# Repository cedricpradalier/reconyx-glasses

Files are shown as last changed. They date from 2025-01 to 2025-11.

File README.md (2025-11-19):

# reconyx-glasses
3D model of lens holders for the [Reconyx HyperFire](https://www.reconyx.com/product/Outdoor_Series?gad_source=1) cameras.

Original camera from the manufacturer's website

This repository includes some work on 3D models dedicated to attach a lens to the camera. The HyperFire camera is a rugged system designed for wild-life monitoring. As a result, the lens focus is fixed to infinity (a few meters away from the camera) and cannot be changed. In our application where the camera takes pictures of images relatively close to the lens, this leads to blurry images. Although this is not a problem in its normal use case, the camera is far-sighted (or even presbyopic) for our very specific use case (probably outside of the camera specifications in the first place) and it needs prescription glasses. 

## Objectives
In our use case, observing toads, tritons and salamanders in wildlife underpass, the effect is the following:

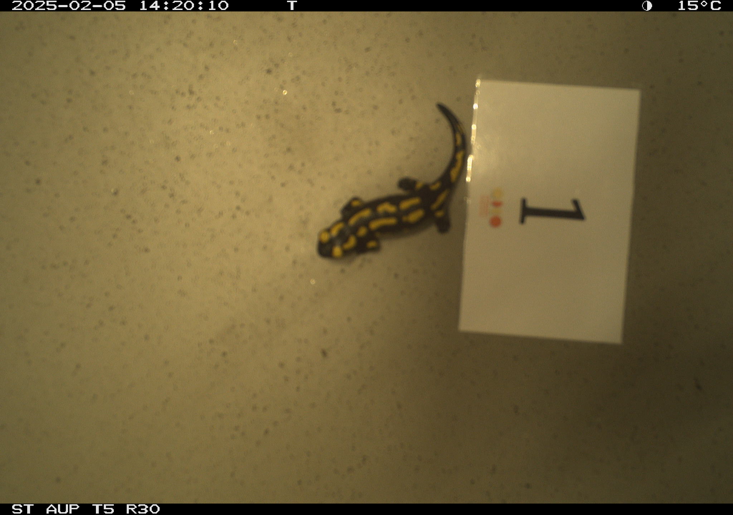
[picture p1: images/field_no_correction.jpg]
Original camera no correction


With the proper correction:

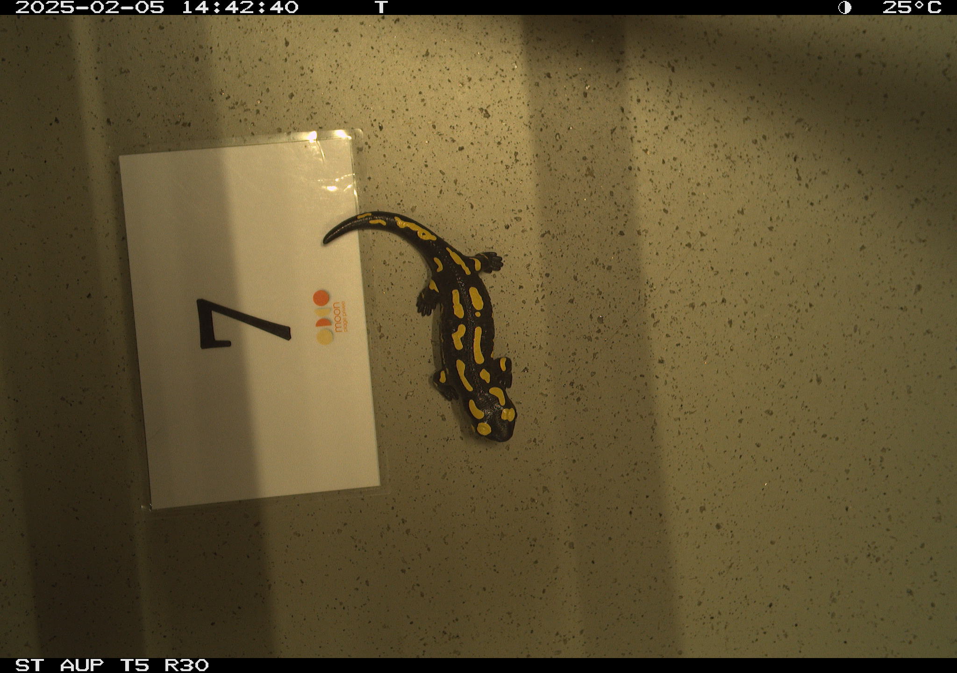
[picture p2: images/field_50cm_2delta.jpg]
Original camera correction


## Designs
The resulting lens holder is designed with [OpenSCAD](https://openscad.org/) to be 3D printed. The SCAD files are in the [scad](scad) folder. The resulting STL files in the [stl](stl) folder.

### Magnetic design
The [third design](stl/reconyx_magnets.stl) is made to be installed on the enclosure and kept in place with magnets. It is not secured as strongly as the previous designs, but much easier to install in cramped condition. This designed is parameterized by the magnet size (10mm diameter, 3mm thickness in the picture below). A 3D view of one version of the design is visible here: 

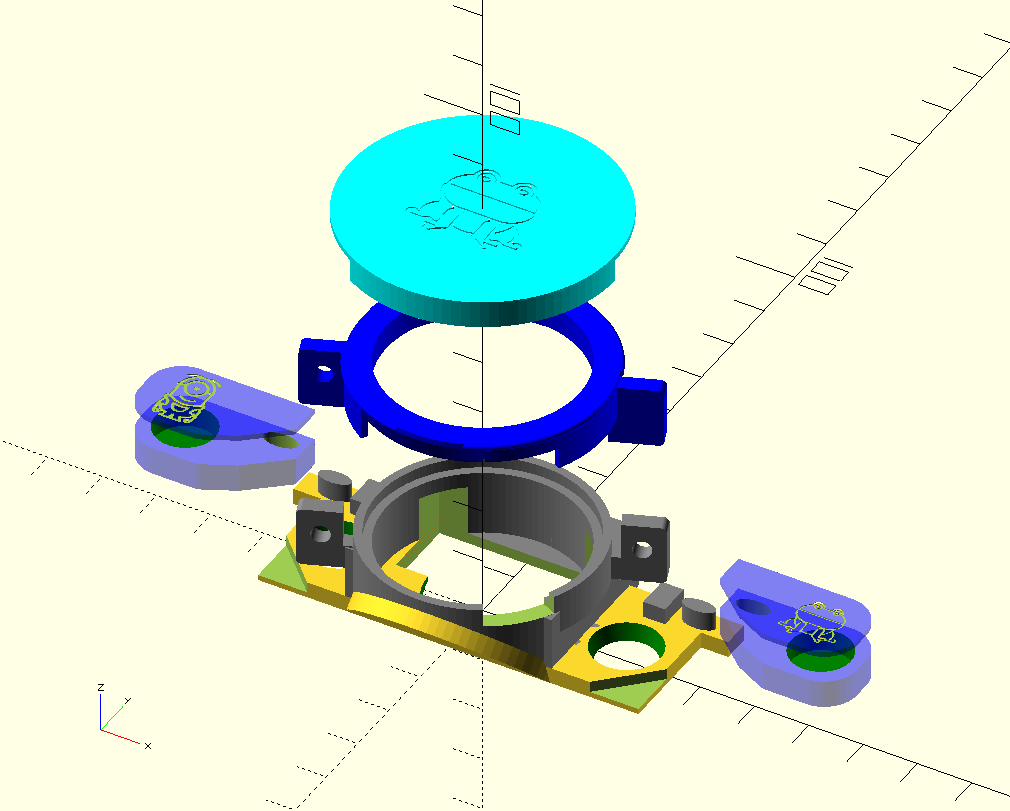
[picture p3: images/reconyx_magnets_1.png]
camera with magnet 1


After printing, the magnets need to be inserted in the side flap (purple in the image above) and the flap cover glued (we use a standard office glue with our PLA print). The flap can then be glued to the main body. 

Once the lens is inserted into the design, the top part(dark blue here) is placed on top of it and rotated into place. A small screw (3mm diameter, 10mm length) is then used to secure the assembly. The top cover (light blue here) is used to protect the lens while the assembly is in storage.

A finalized version, can be seen here with the additional engraving, and installed on the camera

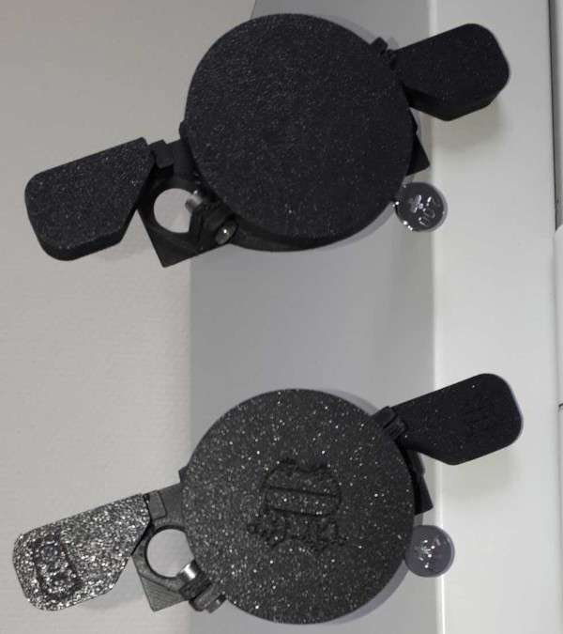
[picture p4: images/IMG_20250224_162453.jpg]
camera with magnet 2


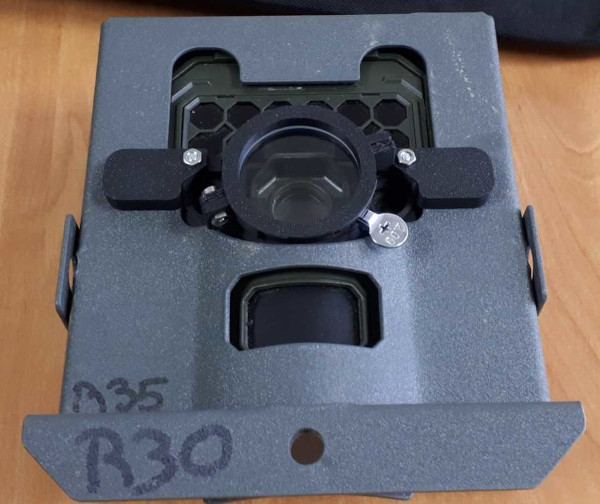
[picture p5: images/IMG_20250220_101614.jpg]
camera with magnet 3


Note that the design was thought to be printed on a filament printer. If you print in a medium that does not rely on support matterial, you can use this [alternative model](stl/reconyx_magnets_no_support.stl). In this design the magnet flap are rigidly attached to the model.

### Mechanically locked design
The [second design](stl/reconyx_box.stl) is kept in place by the [Reconyx enclosure box](https://www.reconyx.com/product/HyperFire-2-Security-Enclosure).

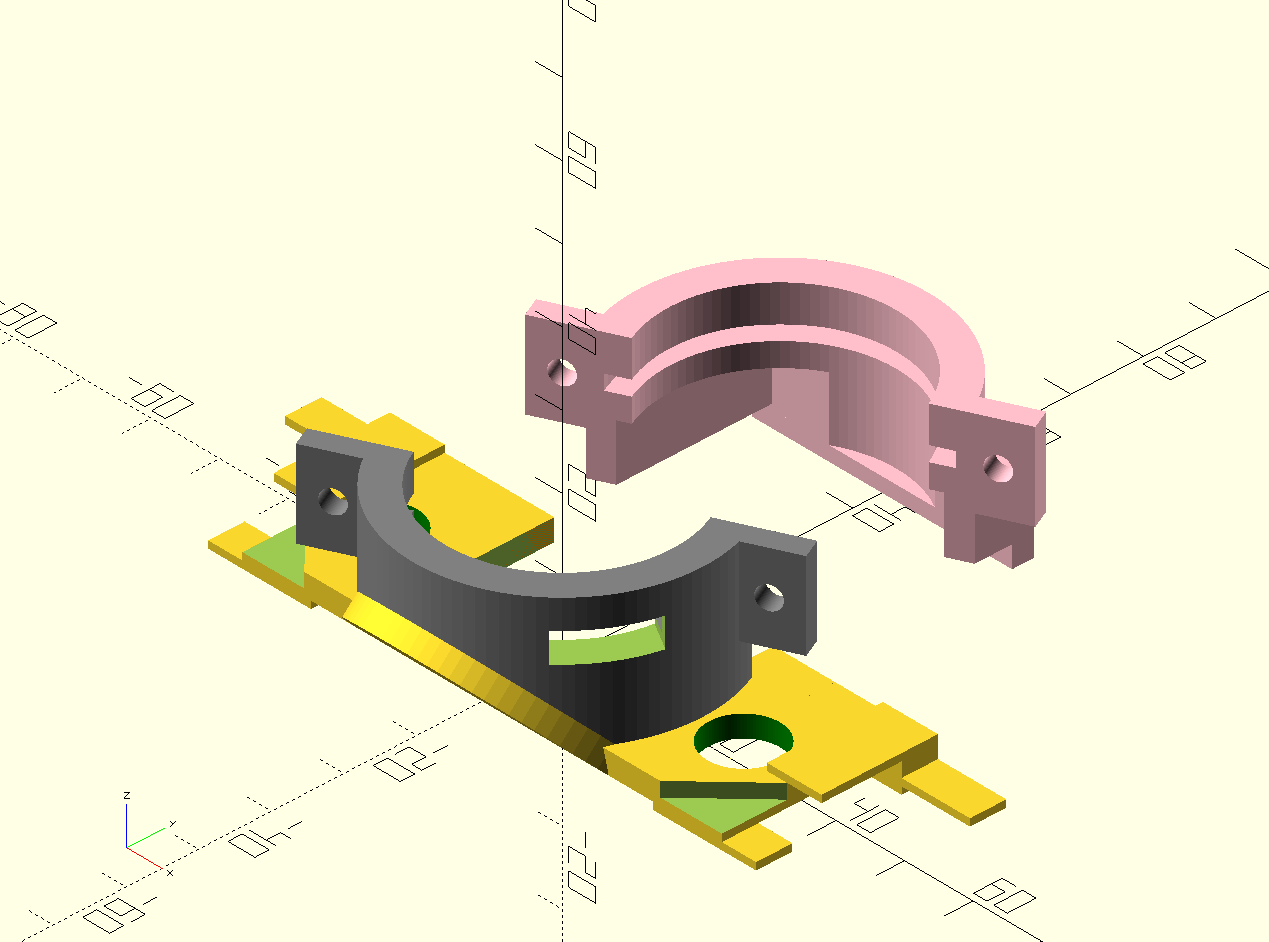
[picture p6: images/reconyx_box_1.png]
camera with clipped lenses CAD


The camera, in its enclosure, with the lens on is displayed here:

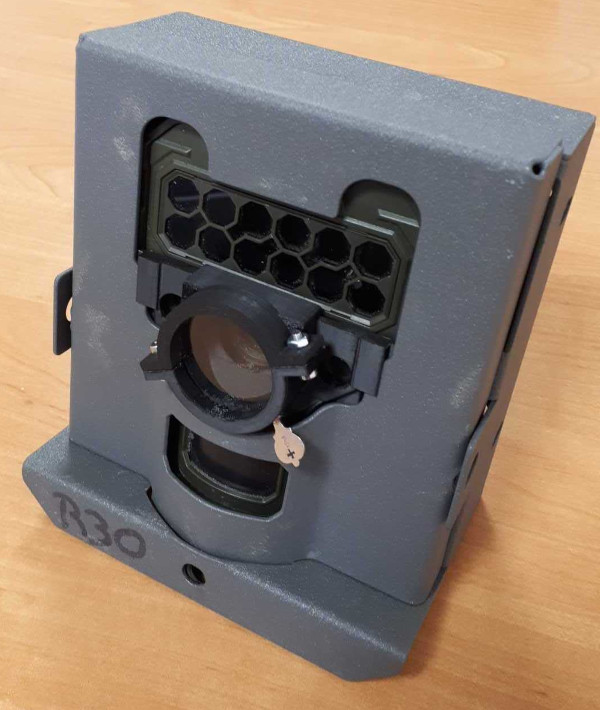
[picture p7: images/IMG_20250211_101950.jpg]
camera with box lens


Adding a tiny rubber band forces the lens in place, while keeping a little bit of flexibility when opening or closing the enclosure:

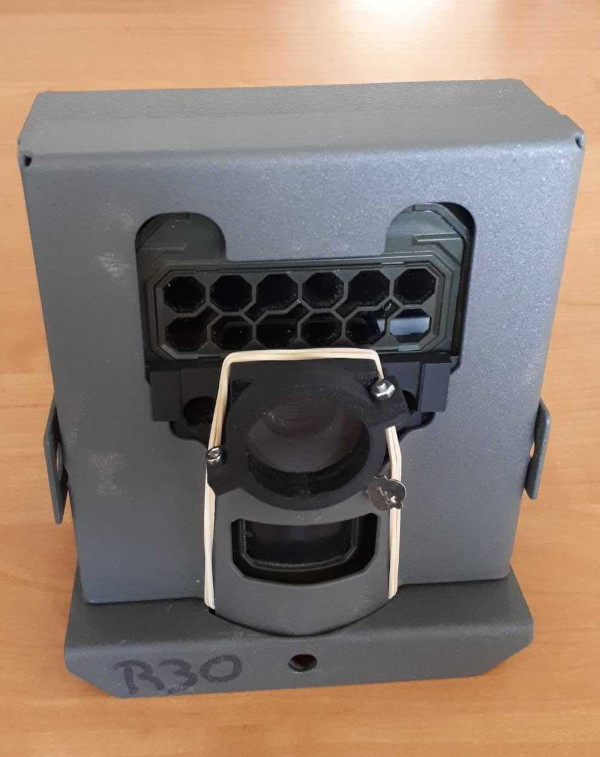
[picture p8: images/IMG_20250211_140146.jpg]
camera with box lens and rubber


### Direct clip design
The [first design](stl/reconyx_clip.stl) clips on the camera without any enclosure. 
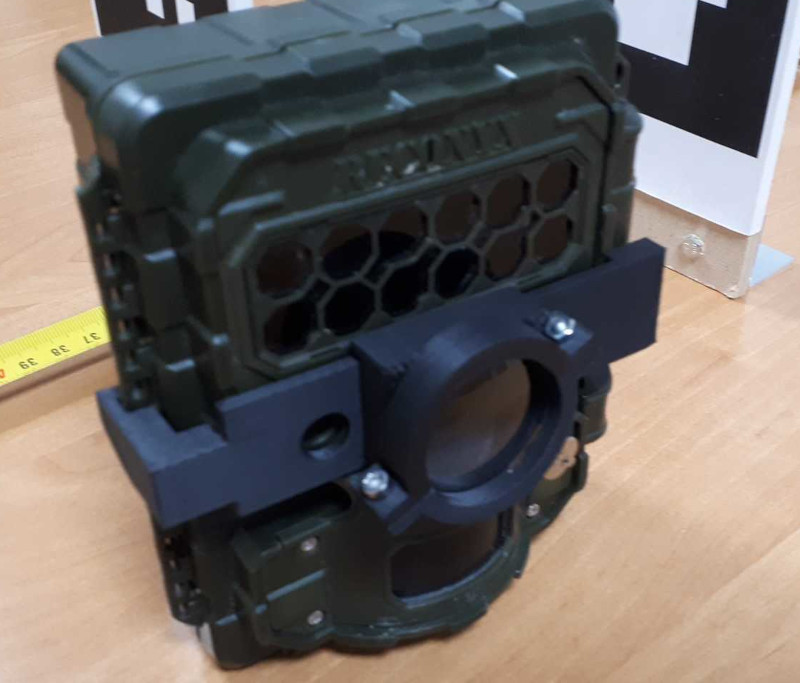
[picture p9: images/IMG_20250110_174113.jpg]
camera with clipped lenses


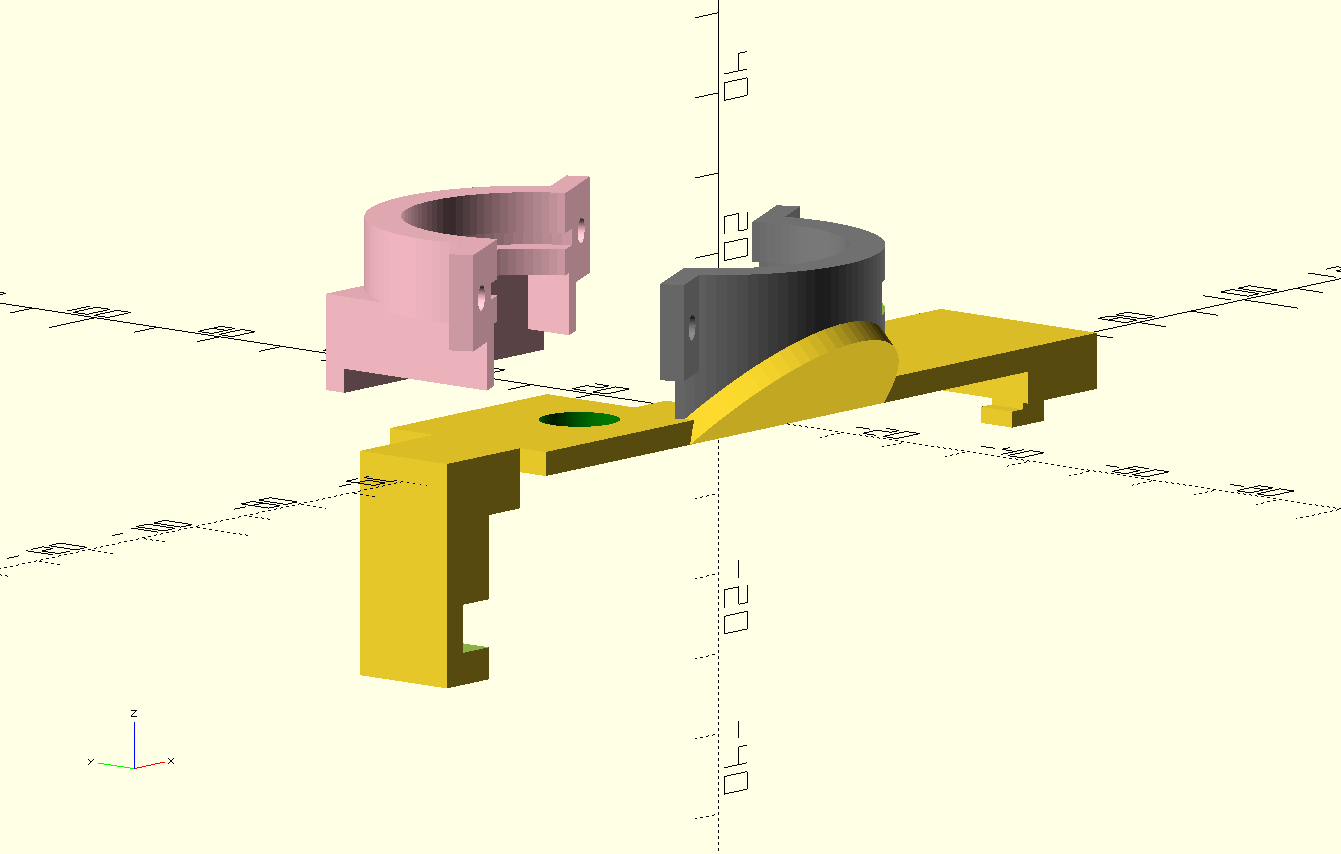
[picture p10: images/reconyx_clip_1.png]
camera with clipped lenses CAD1


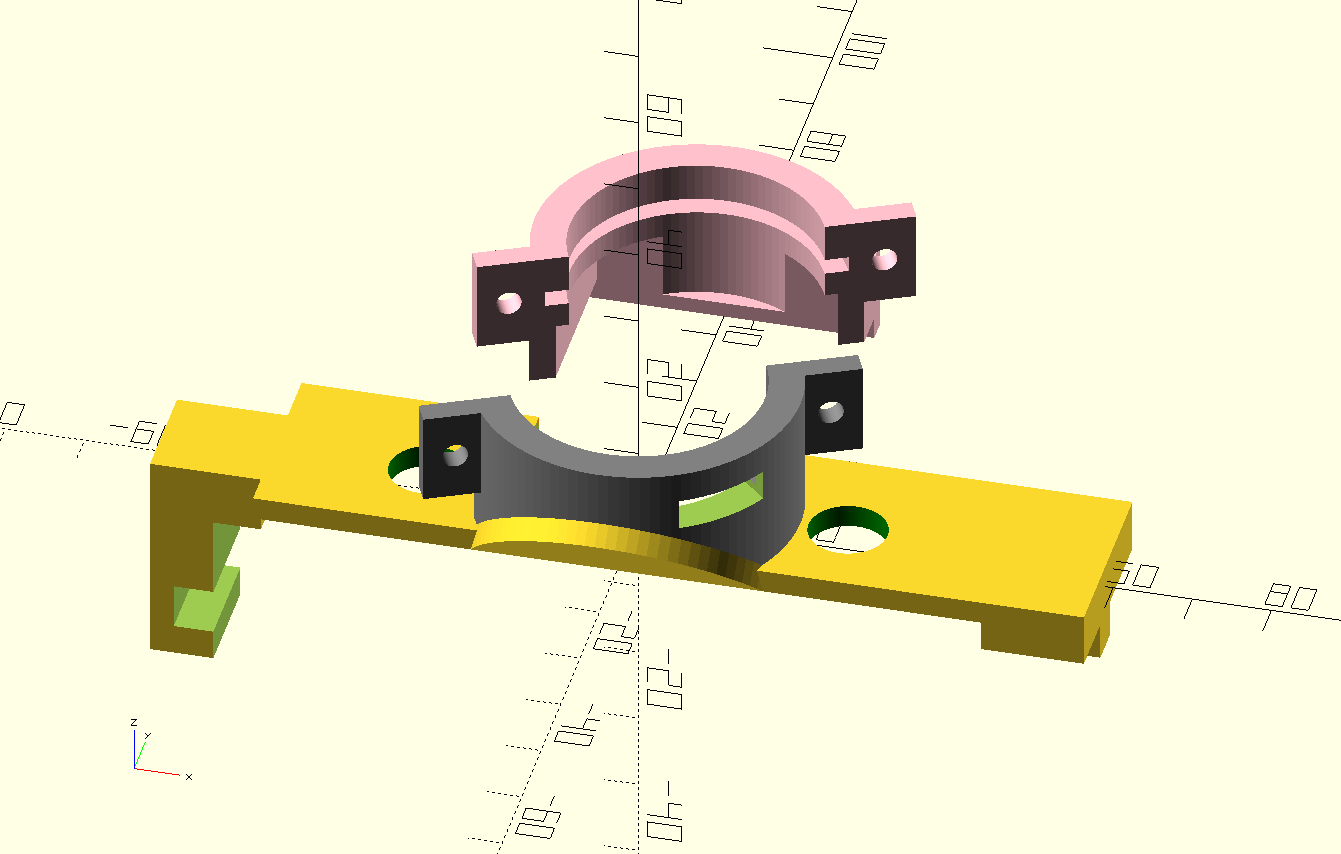
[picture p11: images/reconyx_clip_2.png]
camera with clipped lenses CAD2


## Finding lenses

The proposed model is designed to hold [optometrist test lenses](https://fr.aliexpress.com/item/1703330056.html), which are 38mm wide and 2mm thick. It is relatively easy to find 40mm lenses as [high-school optics material](https://jeulin.com/ovio_fr/pr-323333.html). This can be changed with the Dlens and Tlens variables in the scad files. 

The rule of thumb for selecting the focal or the dioptries is simple. The focal should approximately be equivalent to the distance at which the animals are going to be imaged. The focal resulting from a lens is the inverse of the dioptries, in m. 

Dioptries | Distances
--- | ---
1 | 1.00 m
2 | 0.50 m
2.5 | 0.40 m
3 | 0.33 m
4 | 0.25 m

## Lens testing
After some testing with my [optometrist](https://www.remillyoptic.fr/), this is the effect of choosing glasses from +2.0 to 3.0 dioptries, to observe an object 40cm away from the camera.
Without lenses:
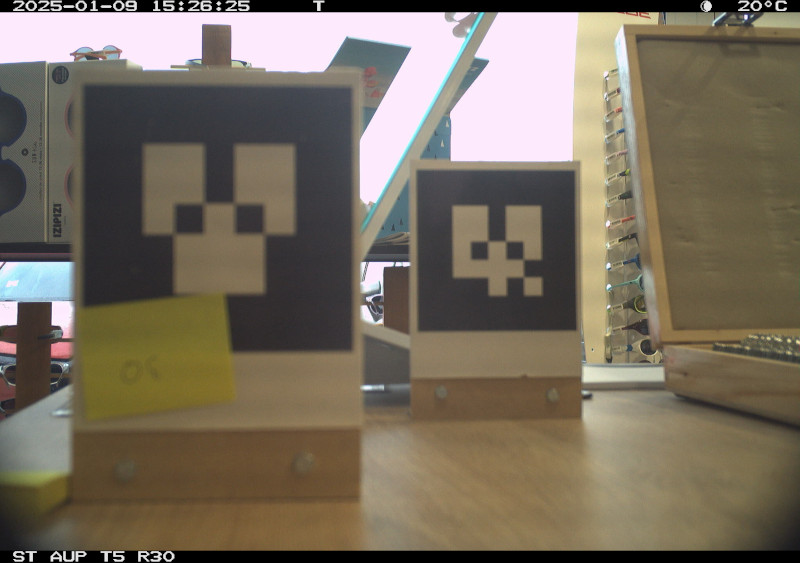
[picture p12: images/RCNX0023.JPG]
Naked lens


With +2.0 correction:
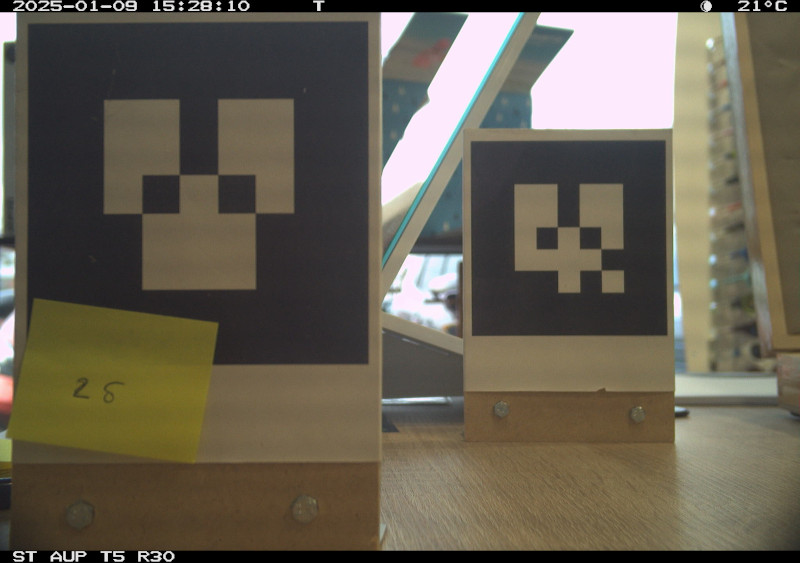
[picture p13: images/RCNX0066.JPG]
+2.0 dioptries


With +2.5 correction:
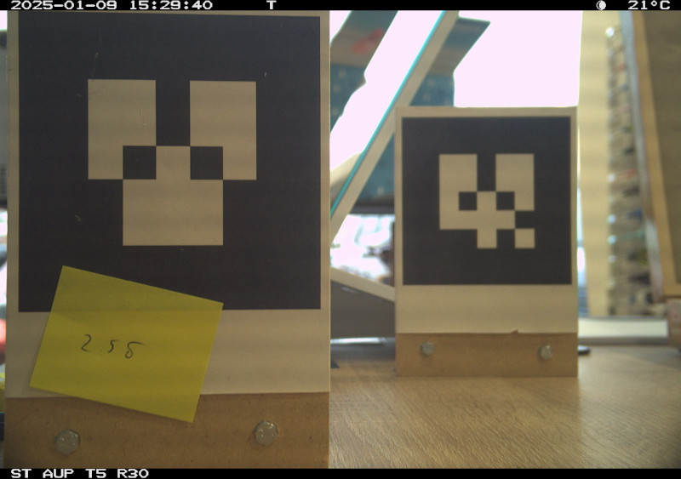
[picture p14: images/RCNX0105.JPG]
+2.5 dioptries


With +3.0 correction:
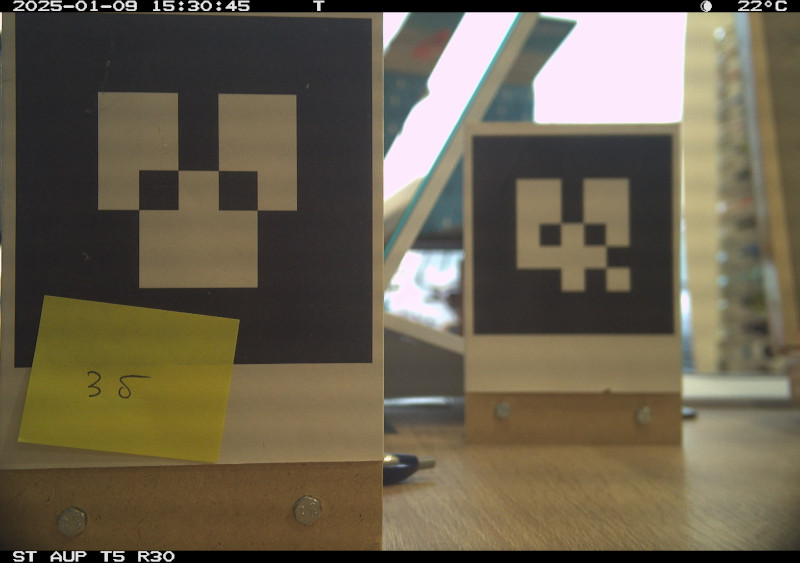
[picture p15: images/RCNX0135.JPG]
+3.0 dioptries


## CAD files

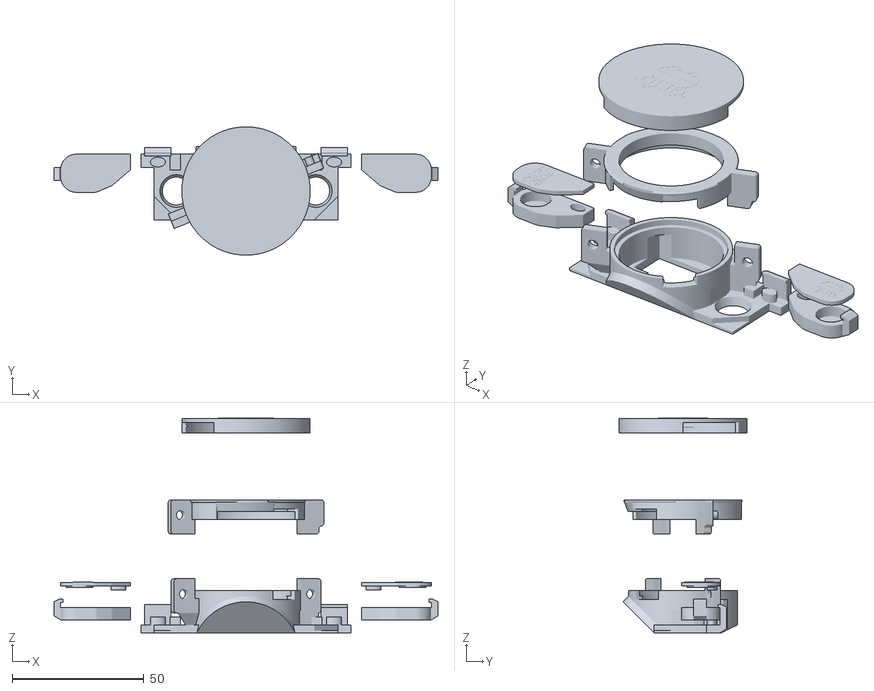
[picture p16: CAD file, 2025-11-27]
stl/reconyx_magnets.stl
146.0 x 48.8 x 81.7

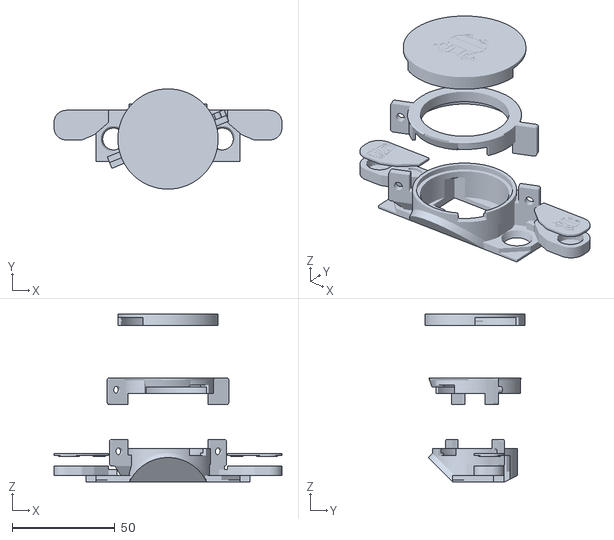
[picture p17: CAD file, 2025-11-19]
stl/reconyx_magnets_no_support.stl
111.0 x 48.8 x 81.6

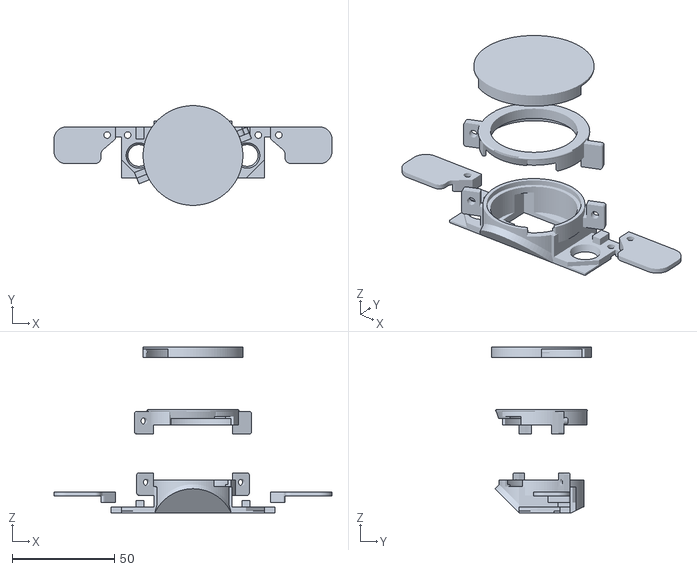
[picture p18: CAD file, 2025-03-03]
stl/reconyx_magnets_large.stl
136.0 x 48.8 x 81.1

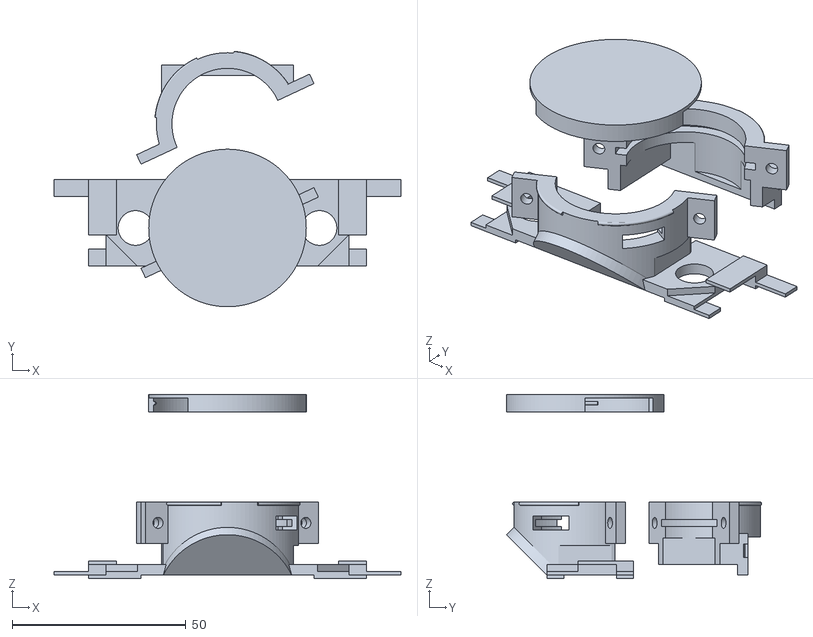
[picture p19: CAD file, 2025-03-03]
stl/reconyx_box.stl
100.0 x 73.6 x 53.0

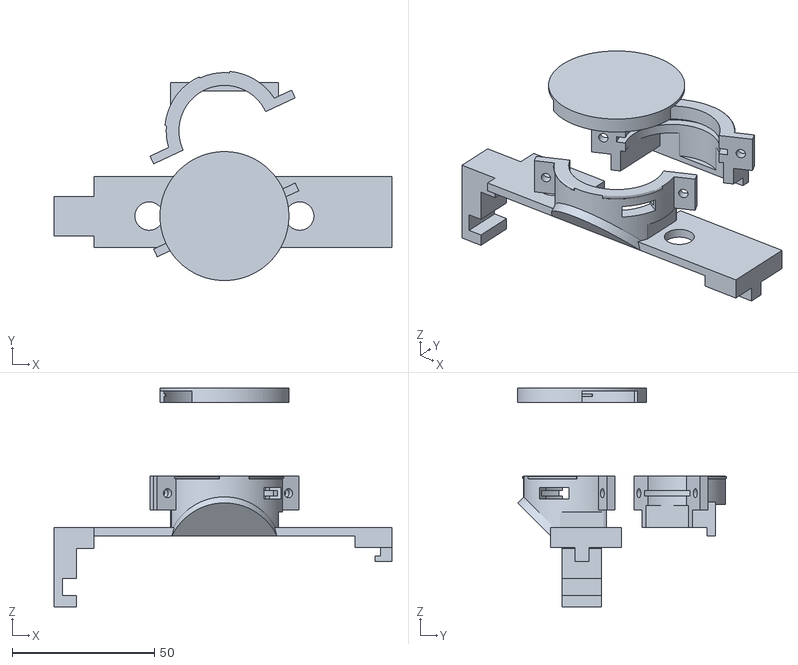
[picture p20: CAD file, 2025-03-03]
stl/reconyx_clip.stl
119.0 x 73.6 x 77.0

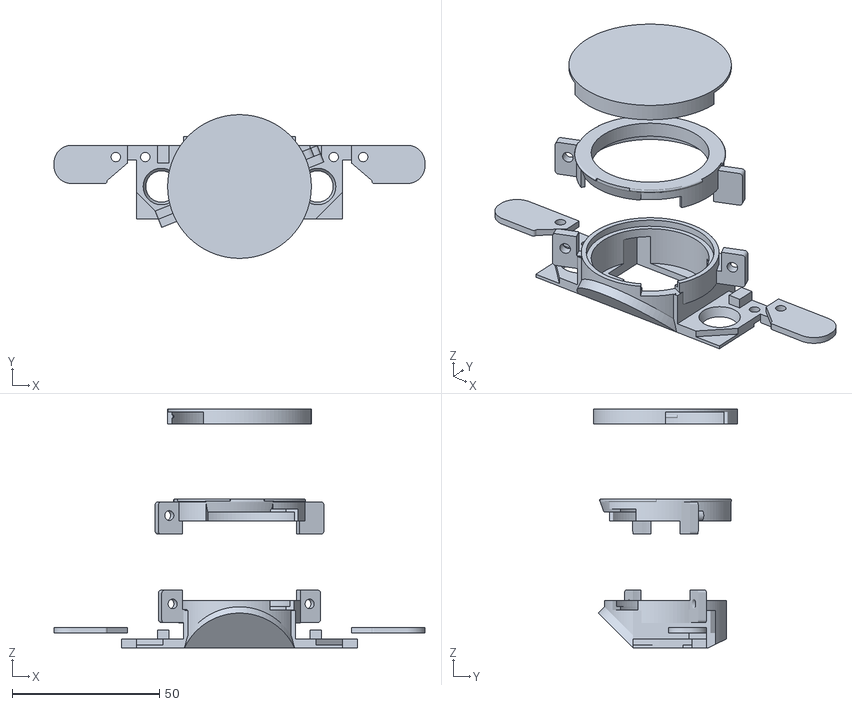
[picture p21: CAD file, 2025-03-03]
stl/reconyx_magnets_small.stl
126.0 x 48.8 x 81.1

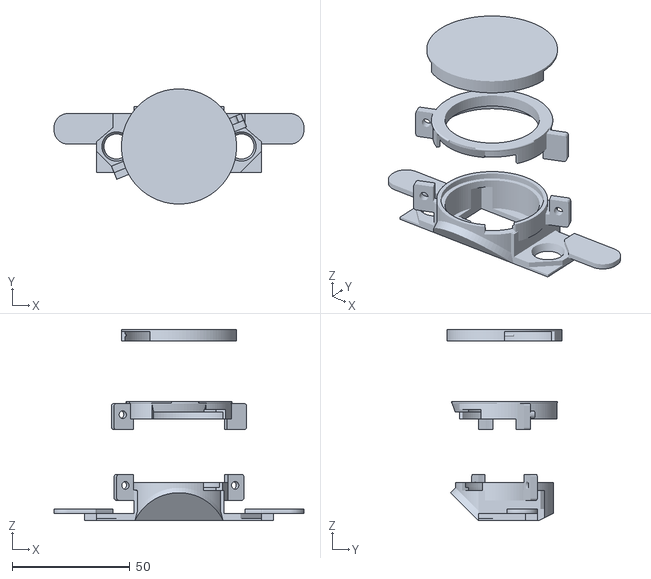
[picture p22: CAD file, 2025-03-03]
stl/reconyx_magnets_attached.stl
106.0 x 48.8 x 81.1

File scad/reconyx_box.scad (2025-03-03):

W=70;


explode=1; // exploded model      
screw=0; // screw cap

  
include <reconyx_common.scad>
// projection() translate([0,0,T+3])
difference() {
    union() {
      translate([0,0,explode?30:0])  rotate([0,0,screw?-30:0]) cap();

        lensholder_attached();

        if (1) {
            translate([0,explode?30:0,0]) lensholder_mobile();
        }

        
        baseplate(W);


        // Flaps to hold the lens holder against the camera enclosure
        translate([W/2-10,-Dobj/2-1,-1+0.001]) cube([15,5,1]);
        translate([W/2-10,-Dobj/2-1+H-5,-1+0.001]) cube([15,5,1+T]);
        translate([W/2,-Dobj/2-1+H-5,0]) cube([15,5,1]);
        translate([-W/2-5,-Dobj/2-1,-1+0.001]) cube([15,5,1]);
        translate([-W/2-5,-Dobj/2-1+H-5,-1+0.001]) cube([15,5,1+T]);
        translate([-W/2-15,-Dobj/2-1+H-5,0]) cube([15,5,1]);
        
        if (1) {
            // little ears to stay attached to the box surface
            translate([W/2-3,-Dobj/2-1+halfdiag,T]) cube([8,H-halfdiag,1]);
            translate([-W/2-5,-Dobj/2-1+halfdiag,T]) cube([8,H-halfdiag,1]);
        }
        

    }
        
    union() {
        // Optional debug cuts
        // translate([-100,-50,6]) cube([200,100,100]);
        // translate([-100,-50,-40]) cube([200,100,40+T+12]);
        // rotate([0,0,-30]) translate([-100,0,6]) cube([200,100,100]);
           
        center_cutout();
              
        corner_cutouts(W);
                
    }
}

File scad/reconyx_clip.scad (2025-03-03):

W=92;

explode=1; // exploded model      
screw=0; // screw cap


include <reconyx_common.scad>

difference() {
    union() {
     translate([0,0,explode?30:0])  rotate([0,0,screw?-30:0]) cap();

        lensholder_attached();

        if (1) {
            translate([0,explode?30:0,0]) lensholder_mobile();
        }

        
        baseplate(W);

        
        // Left leg to attach to reconyx 
        translate([-W/2-14,-footH/2,-28+T]) 
        difference() {
            cube([14,footH,28]);
            union() {
                translate([14-6,-1,-1]) cube([6+1,footH+2,28-7.5+1]);
                translate([14-6-5,-1,4]) cube([6+5+1,footH+2,6]);
            }
        }

        // Right leg to clip in the camera side
        translate([W/2,-Dobj/2-1,-4])
        union() {
            cube([13,H,T+4]);
            translate([9,Dobj/2+1-5/2,-5]) cube([4,5,5]);
            translate([7.001,Dobj/2+1-5/2,-5]) cube([2,5,2]);
        }
    }

               
    union() {
//            translate([-100,-50,6]) cube([200,100,100]);
//            translate([-100,footH/2,-40]) cube([200,100,100]);
        center_cutout();
    }
}

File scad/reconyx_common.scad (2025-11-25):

use <Round-Anything/polyround.scad>

H=25;
H45=17;
T=3;

Dobj=20;
Dled=10;

testLens=1; // type of lens, 1 = 38mm optometric insert, 0 = 40mm
 

Dlens=testLens?38+0.4:40+0.2;
Tlens=2.1;
Dsupport=1.5;
Dholder=testLens?1.5:1.0;

Nlens=1;
Lstart=11;
Lholder_ex=3.5;
Lholder=Lstart+Nlens*(Tlens+1)+Lholder_ex;
footH=H/1.8;
alpha=22;
Lear=11;
earT=3;
earScrew=3.6;

// size of the rotated square removed in the piece corners (in corner_cutouts)
halfdiag=9;
face=halfdiag/(sqrt(2)/2)+0.001;
 

module ear(earW=8,peg=0) {
    if (peg!=0) {
        union() {
            // cube([earW,earT,Lear]);
            rotate([90,0,0]) translate([0,0,-earT]) linear_extrude(earT) {
                polygon(polyRound([[0,-1,1],[0,Lear+1,1],[earW,Lear+1,1],[earW,+2,1],[earW-2,+2,1],[earW-2,-1,1]],20));
            }
            translate([earW-4.0,0,Lear-3-earScrew/2]) rotate([-90,0,0]) cylinder(h=2*earT,r=earScrew/2-0.25,$fn=100);
        }
    } else {
        difference() {
            // cube([earW,earT,Lear]);
            rotate([90,0,0]) translate([0,0,-earT]) linear_extrude(earT) {
                polygon(polyRound([[0,-1,1],[0,Lear+1,1],[earW,Lear+1,1],[earW,-1,1]],20));
            }
            translate([earW-4.0,-1,Lear-3-earScrew/2]) rotate([-90,0,0]) cylinder(h=earT+2,r=earScrew/2,$fn=100);
        }
    }
}

module cap() {
    translate([0,0,Lholder+T-4]) union() {
             color("blue") difference() {
                cylinder(h=5, r=Dlens/2+Dholder+2.2,$fn=100);
                 union() {
                    translate([0,0,-1]) cylinder(h=5, r=Dlens/2+Dholder+0.8,$fn=100);
                     rotate([0,0,0]) translate([0,0,-1]) rotate_extrude(angle=60,$fn=100) {
                        square([Dlens/2+Dholder+3,5]);
                 }
                    rotate([0,0,180]) translate([0,0,-1]) rotate_extrude(angle=60,$fn=100) {
                        square([Dlens/2+Dholder+3,5]);
                 }
                 }
            }
            color("black") 
            for (i=[0:4]) {
                rotate([0,0,-10-90*i]) 
                    rotate_extrude(angle=10,$fn=60) {
                       translate([Dlens/2+Dholder+0.8,2.5,0]) circle(0.5);
                     }
                 }
        }
}

module lensholder_attached() {
    difference() {
        color("grey") union() {
                translate([0,0,Lholder+T-Lear]) 
                    rotate([0,0,180+alpha]) translate([Dlens/2+0.5,0,0]) ear();
                translate([0,0,Lholder+T-Lear]) 
                    rotate([0,0,alpha]) translate([Dlens/2+0.5,-earT,0]) ear();
                
                // Small rim to hold lens cap
                translate([0,0,T+0.001]) {
                    rotate([0,0,180+alpha]) 
                        rotate_extrude(angle=60,$fn=100) {
                           translate([Dlens/2+Dholder,Lholder-0.5,0]) circle(0.5);
                         }
                    rotate([0,0,180+alpha+90]) 
                        rotate_extrude(angle=60,$fn=100) {
                           translate([Dlens/2+Dholder,Lholder-0.5,0]) circle(0.5);
                         }
                 }
                
                 translate([0,0,T+0.001]) difference() {
                    rotate([0,0,180+alpha]) rotate_extrude(angle=180,$fn=100) {
                        square([Dlens/2+Dholder,Lholder]);
                     }
                    color("green") union() {
                        translate([0,0,-1]) cylinder(h=Lholder+2,r=Dlens/2-Dsupport,$fn=100);
                        translate([19,-Dobj/2-1,0]) cube([2,H,5.5]);
                        translate([-21,-Dobj/2-1,0]) cube([2,H,5.5]);
                        for (i = [0:Nlens-1]) {
                            translate([0,0,Lstart+i*(Tlens+1)]) cylinder(h=Tlens,r=Dlens/2,$fn=100);
                        }
                        translate([0,-Dobj/2-1,0]) rotate([-45,0,0]) translate([-Dobj,-H45,-20]) cube([2*Dobj,H45,20]);
                    }
                }
            }
            if (testLens) {
                // Opening for test lens handle
                Whandle=12;
                rotate([0,0,-30]) translate([Dlens/2-6,-Whandle/2,Lholder+T-(Tlens+2+Lholder_ex)+0.002]) union() {
                    cube([10,Whandle,(Tlens+2)]);
                    //translate([0,Whandle,0]) cube([10,Whandle,Tlens]);
                }
            }
    }
}

module lensholder_mobile() {
    color("pink") 
            //translate([0,0,2*(Lholder+T)+0.5]) rotate([180,0,0])
            
            union() {
                translate([0,0,Lholder+T-Lear]) 
                    rotate([0,0,alpha]) translate([Dlens/2+0.5,0,0]) ear();
                translate([0,0,Lholder+T-Lear]) 
                    rotate([0,0,180+alpha]) translate([Dlens/2+0.5,-earT,0]) ear();
                
                // Small rim to hold lens cap
                translate([0,0,T+0.001]) {
                    rotate([0,0,alpha]) 
                        rotate_extrude(angle=60,$fn=100) {
                           translate([Dlens/2+Dholder,Lholder-0.5,0]) circle(0.5);
                         }
                    rotate([0,0,alpha+90]) 
                        rotate_extrude(angle=60,$fn=100) {
                           translate([Dlens/2+Dholder,Lholder-0.5,0]) circle(0.5);
                         }
                 }
                 
                translate([0,0,T-0.001]) difference() {
                    // Main lens holder (pink side)
                    union() {
                        translate([0,0,8]) rotate([0,0,alpha]) rotate_extrude(angle=180,$fn=100) {
                         square([Dlens/2+Dholder,Lholder-8]);
                     }
                     // Bottom cube (pink side)
                     difference() {
                         union() {
                            translate([-19,-Dobj/2-1,0]) cube([38,H+5,T+1+5]);
                             translate([-19,-Dobj/2-1+H,-T]) cube([38,5,T]);
                         }
                         union() {
                            rotate([0,0,180+alpha]) translate([-30,0,-1]) cube([60, H, T+1+10]);
                            // Little grooves to hold the rubber band
                            translate([-19,-Dobj/2-1+H+5,2]) cylinder(h=4,r=1.5);
                            translate([19,-Dobj/2-1+H+5,2]) cylinder(h=4,r=1.5);
                         }
                     }
                     
                 }
                 // Cut-out in the pink side
                    color("green") union() {
                        translate([0,0,-1]) cylinder(h=Lholder+2,r=Dlens/2-Dsupport,$fn=100);
                        // Lens groove
                        for (i = [0:Nlens-1]) {
                            translate([0,0,Lstart+i*(Tlens+1)]) cylinder(h=Tlens,r=Dlens/2,$fn=100);
                        }
                        
                        translate([-16,-10,-0.75]) cube([32,H/2+10+1.5,T+1.5+4]);
                    }
                }
            }
}

module baseplate(width) {
    difference() {
            union() {
                translate([-width/2,-Dobj/2-1,0]) cube([width,H,T]);
                //translate([0,-Dobj/2-1,0]) rotate([-45,0,0]) translate([-Dobj,-H45,0]) cube([2*Dobj,H45,T]);
                difference() {
                    translate([0,0,-Dobj/2-1+T*sqrt(2)]) rotate([-45,0,0]) 
                        translate([0,0,-T]) scale([1,sqrt(2),1]) 
                        cylinder(h=T,r=Dlens/2+Dholder,$fn=100);
                    translate([-Dlens/2-2.5,-Dlens/2-2.5,-Dlens*sqrt(2)+0.001]) cube([Dlens+5,Dlens+5,Dlens*sqrt(2)]);
                    
                }
            }
            union() {
                color("green") translate([0,0,-1]) cylinder(h=T+2,r=Dobj/2,$fn=100);
                
                color("green") translate([-26.5,0,-1]) cylinder(h=T+2,r1=Dled/2,r2=(Dled+3)/2,$fn=100);
                color("green") translate([26.5,0,-1]) cylinder(h=T+2,r1=Dled/2,r2=(Dled+3)/2,$fn=100);
                color("orange") translate([-16,0,-0.75]) cube([32,H/2+5,T+1.5]);
                translate([-16,-T*sqrt(3),-0.75]) rotate([-60,0,0]) cube([32,H/2+1.5,T*5]);
            }
        }
}

module corner_cutouts(width) {
            // Oblique corner cut-out
        translate([width/2,-Dobj/2-1,T-2]) 
            rotate([0,0,45]) translate([-face/2,-face/2,0]) cube([face,face,3]);
        translate([-width/2,-Dobj/2-1,T-2]) 
            rotate([0,0,45]) translate([-face/2,-face/2,0]) cube([face,face,3]);
}

module center_cutout() {
    translate([-16,0,-0.75]) cube([32,H/2+1.5,T+1+8]);
}

module handle(w,h,radius) {
    translate([-w/2,0,0]) {
        cylinder(h,r=radius,$fn=30);
        translate([w,0,0]) cylinder(h,r=radius,$fn=30);
        translate([w/2,0,h]) rotate([90,0,0]) rotate_extrude(angle=180,$fn=30) {
            translate([w/2,0,0]) circle(r=radius);
        }
    }
}

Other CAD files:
scad/reconyx_magnets.scad

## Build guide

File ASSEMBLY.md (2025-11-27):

# Reconyx-glasses: Assembly process

This page illustrates the assembly process for the 3D-printed model in the [third design](stl/reconyx_magnets.stl). These assembly instructions may need to be adjusted to minor design changes, but the steps should still be valid.

The process assumes that you printed all the components and procured two round magnets (10mm diameter, 3mm thickness). The dimensions have been validated while printing on a Bambulab PS1, with 0.16mm layers and PLA plastics. 

All the components are visible here:

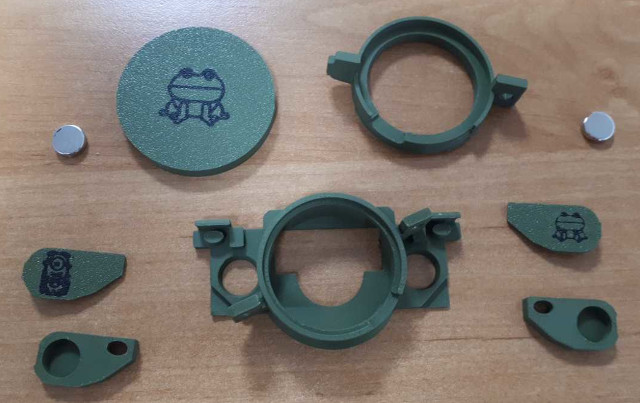
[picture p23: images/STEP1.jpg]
Assembly STEP1


The first stage consist in attaching the magnet holders to the base plate of the lens holder. The magnet holders are just inserted on the elliptical pivots. Depending on the printing, it may fit more or less smoothly.

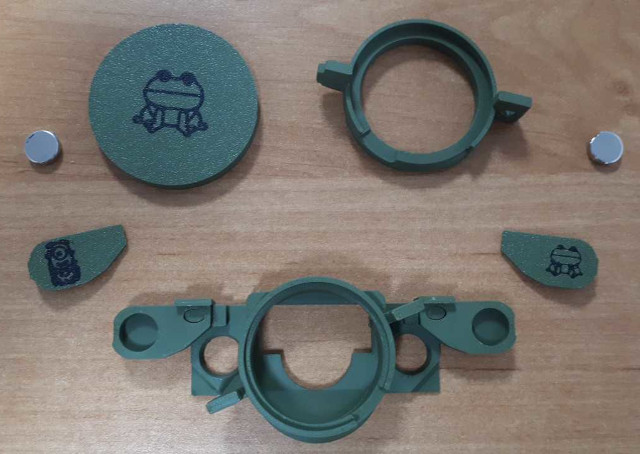
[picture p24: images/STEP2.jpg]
Assembly STEP2


The magnets are then dropped into place:

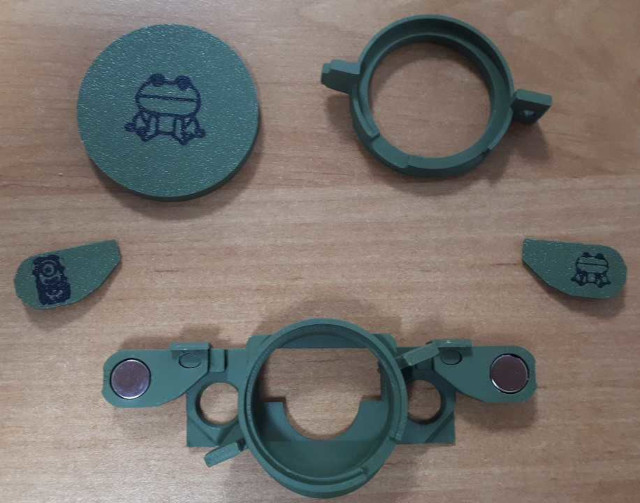
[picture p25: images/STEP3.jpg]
Assembly STEP3


And the magnet cover is clipsed in place:

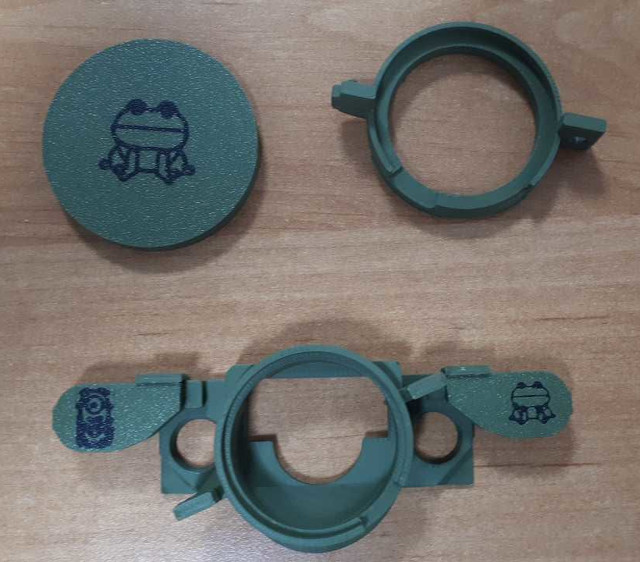
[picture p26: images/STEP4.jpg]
Assembly STEP4


The lens can then be placed in position, and the lens holder placed on top of it (the lens is absent in this picture). 

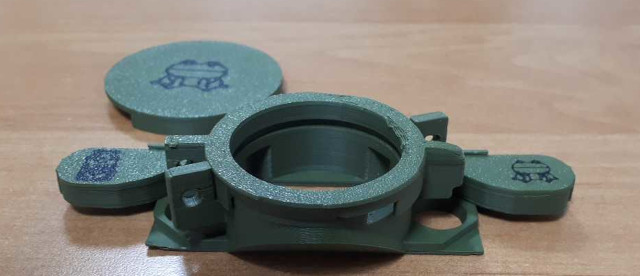
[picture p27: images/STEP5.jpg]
Assembly STEP5


Rotate the lens holder to insert the pivot in the corresponding hole, and use a small screw (3mm diameter, 10mm length) to lock the assembly in place.

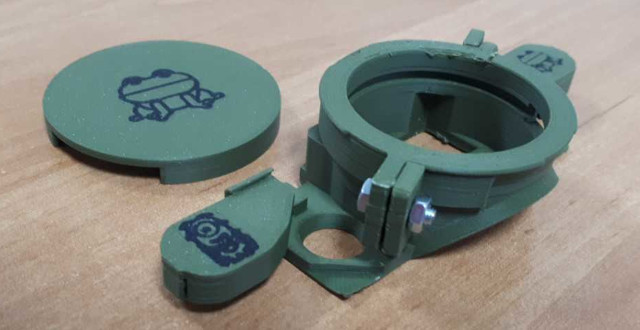
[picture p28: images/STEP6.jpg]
Assembly STEP6


The "glasses" are ready to be attached to the Reconyx enclosure.

For transport and storage the lens cover can be inserted and twisted into place:
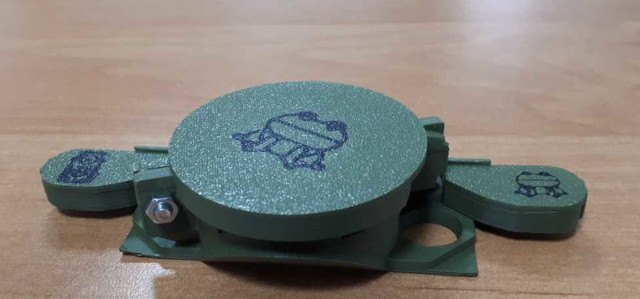
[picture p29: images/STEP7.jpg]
Assembly STEP7


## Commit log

2025-01-31 Initial import
    [reconyx_box.scad, reconyx_clip.scad, reconyx_clip.stl]
2025-01-31 Updated lens description
2025-01-31 Added lens links
2025-01-31 Added first version of box holder
    [reconyx_box.stl]
2025-02-07 Tested first version of design compatible with the protection box.
    [reconyx_box.scad, reconyx_box.stl]
2025-02-07 Added reference to camera box
2025-02-11 Workable version with protection box
    [reconyx_box.scad, reconyx_box.stl]
2025-02-11 Prepared model for using OTS lenses
    [reconyx_box.scad, reconyx_box.stl]
2025-02-12 Added cap, and rim, to be tested
    [reconyx_box.scad, reconyx_box.stl]
2025-02-13 Tested working cap
    [reconyx_box.scad, reconyx_box.stl]
2025-02-13 Added cap to clippable model. Commented model.
    [reconyx_box.scad, reconyx_box.stl, reconyx_clip.scad, reconyx_clip.stl]
2025-02-14 Added alternative design with magnet holders
    [reconyx_magnets.scad, reconyx_magnets.stl]
2025-02-14 Resized magnet holders
    [reconyx_magnets.scad, reconyx_magnets.stl]
2025-02-14 Modularised different parts and enforced code reuse
    [reconyx_box.scad, reconyx_clip.scad, reconyx_common.scad, reconyx_magnets.scad]
2025-02-14 Finished modularization
    [reconyx_box.scad, reconyx_clip.scad, reconyx_common.scad, reconyx_magnets.scad]
2025-02-17 Added tolerance to lens diameter
    [reconyx_common.scad, reconyx_magnets.scad, reconyx_magnets.stl]
2025-02-18 Added handles on magnet flaps, potentially to secure the lens to the box
    [reconyx_common.scad, reconyx_magnets.scad, reconyx_magnets.stl]
2025-02-18 Increased screw tolerance
    [reconyx_common.scad, reconyx_magnets.scad, reconyx_magnets.stl]
2025-02-18 Major change of design to print the lens holder in one part
    [reconyx_common.scad, reconyx_magnets.scad, reconyx_magnets.stl]
2025-02-18 Conical led opening, lens support reduction, increased space above lens, mostly for the lens handle
    [reconyx_common.scad, reconyx_magnets.scad, reconyx_magnets.stl]
2025-02-19 Validated model for magnetic attachment. To be tested in the field
    [reconyx_box.scad, reconyx_common.scad, reconyx_magnets.scad, reconyx_magnets.stl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]
2025-02-20 Modified flaps to enclose the magnets
    [reconyx_magnets.scad]
2025-02-23 Added engraving and SVG files (with licences in the comment)
    [reconyx_common.scad, reconyx_magnets.scad]
2025-03-03 Finalized magnet model
    [reconyx_magnets.scad]
2025-03-03 Moved lens testing to the bottom of the page
2025-11-19 Latest update for more robust design, easier to print as well
    [reconyx_common.scad, reconyx_magnets.scad]
2025-11-19 Added final STL as a tracked file
    [reconyx_magnets.stl]
2025-11-19 Updated readme with assembly instructions and updated STL files
    [reconyx_magnets.scad, reconyx_magnets.stl, reconyx_magnets_no_support.stl]
2025-11-25 Added clipsable plug concept, but not rigid enough
    [reconyx_magnets.scad]
2025-11-25 Added relief print of the engraving, for bicolor printing. Added a bolder version of the toad, otherwise our bambulab slicer would not draw the contours.
    [reconyx_common.scad, reconyx_magnets.scad, reconyx_magnets.stl]
2025-11-26 Working clipping mechanism for glue-less assembly.
    [reconyx_magnets.scad, reconyx_magnets.stl]
2025-11-27 Added assembly instructions
    [reconyx_magnets.scad, reconyx_magnets.stl]
